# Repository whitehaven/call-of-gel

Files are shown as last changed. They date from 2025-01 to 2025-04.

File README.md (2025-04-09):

# call-of-gel

Trials to create ultrasound-compatible models for training purposes.

## Project Aims

It is important to note the primary goal is to create realistic models to generate high-fidelity practice repetitions linking Seldinger technique motor skills to live ultrasound navigation. This complex skill is the most challenging component of Internal Medicine procedures, especially when practiced at different scales and depths with different tools (arterial vs IJ lines). The specifics of individual procedures are relatively simple in comparison, e.g., all-in-one radial arterial line "darts" vs needle-and-wire kits.

- Create realistic ultrasound training materials approximating human tissue and vessels
  - target procedures are CVC and arterial line placement
  - this could be expanded to paracentesis, thoracentesis, and possibly lumbar puncture
- Acceptable candidate gel formulation would be:
  - nontoxic to create and require minimal materials beside  those found in medical contexts
  - nontoxic to handle
  - provide realistic ultrasonographic return
  - facilitate durable fluid-fillable lumens
    - these may be composed of surgical tubing or other components, but ideally they would be simple cast voids in the gel model which could be filled
- Ideal but non-critical characterstics:
  - Self-healing characteristic to lengthen longevity of created lumens
  - Recyclable/re-moldable by heating or other simple methods

### Future Directions

Requirements for Usable Models:

- [ ] multi-vessel gel mold

Investigational:

- [ ] consider alternative additives for echogenicity: sandblasting media (walnut shells, glass beads)
- [ ] consider agarose as gellant (admittedly no clear advantage other than smell)
- [ ] consider platicized PVC as alternative due to lack of odor and refrigeration requirement (complicated by creation requirement for vacuum chamber and lab-grade heating element at least)
- [ ] consider geometry of cast void which could be used as simulated vessel; otherwise obtain suitable vessel lumen material
- [ ] consider lumen material

## Trial 1 - **2025-01-16**

Mixture DOE with central augmentation. Assess `texture`, `echogenicity`, and `vessel_veracity`, all of which are required for an ultrasound model or "phantom." `Usability` characteristic was added post-hoc due to trouble with formation of tough cap in some cases that severely limited the utility of the sample without harming the gel's echogenicity in other areas.

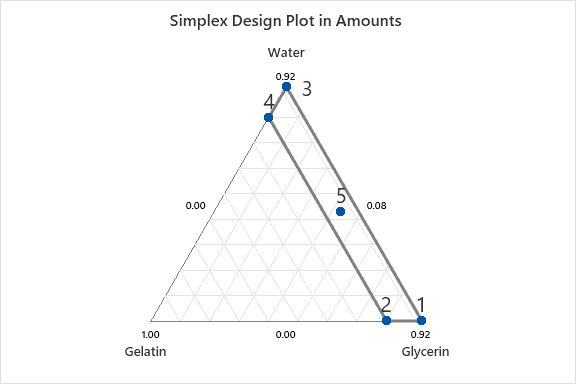
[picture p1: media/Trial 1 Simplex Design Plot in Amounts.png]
Trial 1 Simplex Design Plot


### Protocol

1. Base mixtures combined in 8oz party cup.
1. Gelatin mixed in to base mixture cold and slowly. Total mass for each was 150g.
1. Gelatin heated to 120-140F in double-boiler
1. Vessel mold (custom-thermoformed platicized PVC tubing suspended from baling wire in L-shape to create fillable simulated vessel) placed into each mixture.
1. When temperature achieved, cooled immediately to 40F for 8h.
1. Cast void lumens were filled with water by needle
1. Phillips Xtend unit was used to assess echogenicity

#### Deviations

1. Trial 1-5 took on a dense applesauce-like texture before insertion of vessel mold. The surface of the mixture had to be physically displaced by the mold. It reformed over the top spontaneously.
1. Trial 1-1 and 1-2 remained gooey after all other samples hardened. They are oily to touch and pull apart like thick applesauce. It is evident that glycerin content should not be greater than 50%.
1. Trial 1-4 was difficult to mix and generated extremely dense foam at the top during heating. It appeared to have retained air bubbles and was impenetrable to ultrasound due to scattering.
1. Trial 1-5 also generated dense foam, but the layer was about 2mm. It seemed to cause scattering as well, but much less so.

### Results

| StdOrder | RunOrder | PtType | Blocks | Water | Gelatin | Glycerin | test_g | water_g | gelatin_g | glycerin_g | resilience | echogenicity | usability | vessel_quality |
|----------|----------|--------|--------|-------|---------|----------|--------|---------|-----------|------------|------------|--------------|-----------|----------------|
| 1        | 1        | 1      | 1      | 0.00  | 0.08    | 0.92     | 150    | 0       | 12        | 138        | 1          | 1            | 0         | 1              |
| 2        | 2        | 1      | 1      | 0.00  | 0.20    | 0.80     | 150    | 0       | 30        | 120        | 1          | 1            | 1         | 1              |
| 3        | 3        | 1      | 1      | 0.92  | 0.08    | 0.00     | 150    | 138     | 12        | 0          | 2          | 1            | 3         | 2              |
| 4        | 4        | 1      | 1      | 0.80  | 0.20    | 0.00     | 150    | 120     | 30        | 0          | 3          | 1            | 1         | 2              |
| 5        | 5        | 0      | 1      | 0.43  | 0.14    | 0.43     | 150    | 65      | 21        | 65         | 3          | 2            | 2         | 2              |

(Where `test_g` is test mass in grams, and each ingredient specified as *_g is component mass.)

### Analysis

#### Mixture Plots

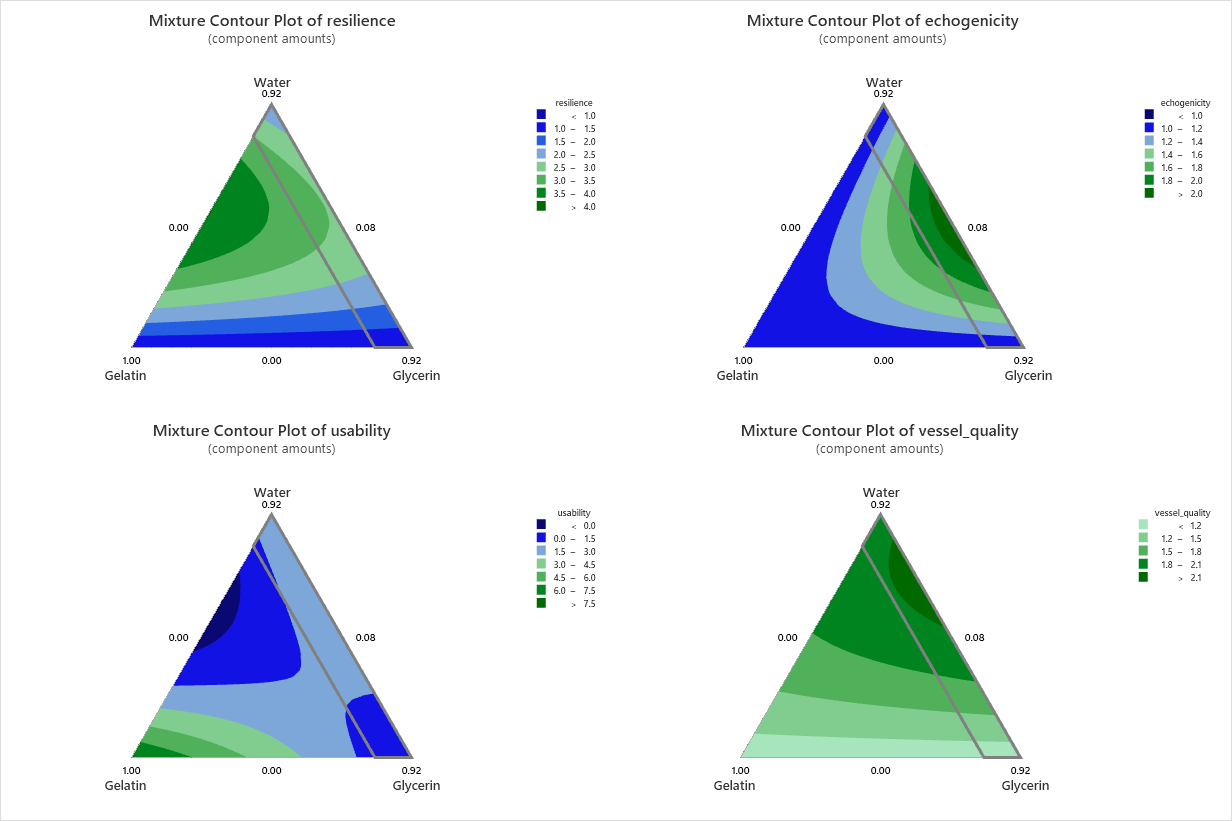
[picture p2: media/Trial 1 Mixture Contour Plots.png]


##### Conclusions

- Glycerin may help echogenicity but degrades resilience beyond 50%
- Echogenicity overall is pretty poor - additives needed

#### Response Optimization based on Trial 1

##### Parameters

|  | Goal         | Lower   | Target | Upper | Weight | Import |
|--------------|---------|--------|-------|--------|--------|---|
| resilience   | Maximum | 1      | 3     | 3      | 0.5*    | 1 |
| echogenicity | Maximum | 1      | 3     | 3      | 1      | 1 |
| usability    | Maximum | 0      | 3     | 3      | 0.5*    | 1 |
| vessel_quali | Maximum | 1      | 3     | 3      | 1      | 1 |

\* Weighting function modified to positive logarithmic shape to reflect that once adequate values are achieved, further pursuit of improvement is increasingly unimportant. Importance was not changed as the gel is unusable if these requirements are not met.

##### Global Solution

| Components |   |          |
|------------|---|----------|
| Water      | = | 0.557576 |
| Gelatin    | = | 0.08     |
| Glycerin   | = | 0.362424 |

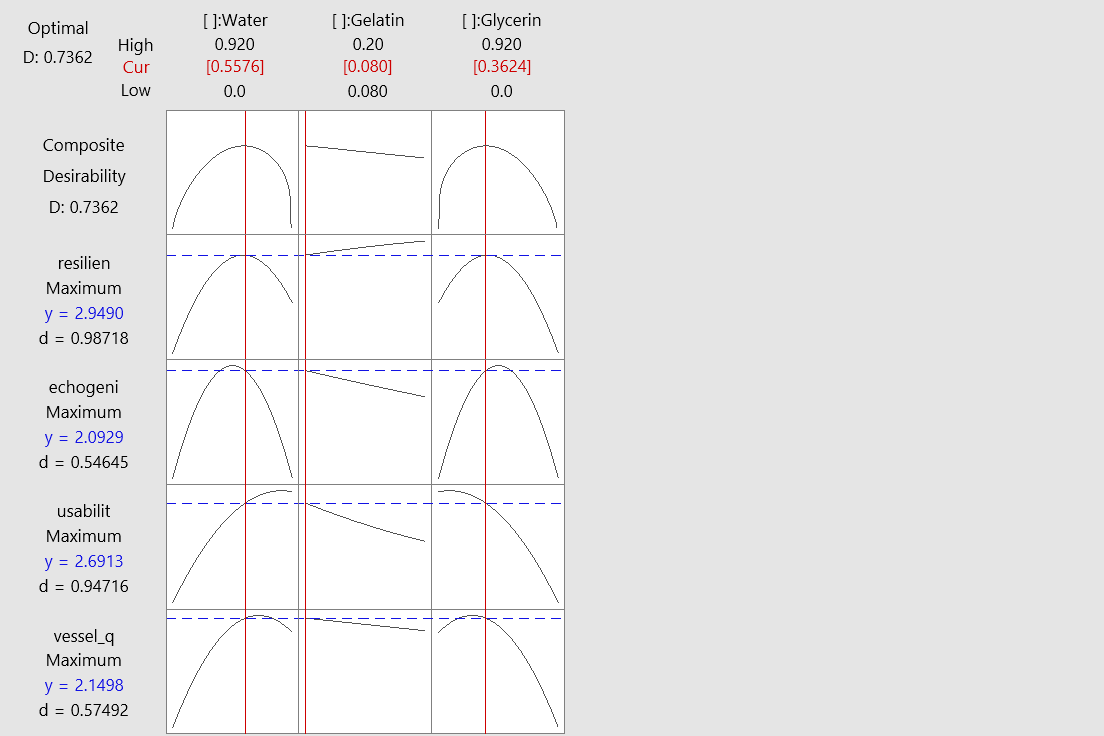
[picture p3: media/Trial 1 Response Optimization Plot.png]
Response Optimization Plot


*Addendum 2025-02-08:* More sophisticated analysis with JMP post-hoc with echogenicity electively removed due to low variance suggests the ideal mixture is as follows:

[JMP analysis report, captured at optimal solution](<media/trial 1-rereanalysis - Fit Least Squares.htm>).

Per JMP, global solution is instead:

| Components |   |          |
|------------|---|----------|
| Water      | = | 0.92 |
| Gelatin    | = | 0.08     |
| Glycerin   | = | 0.0 |

### Future Directions

- Glycerin should be no higher than 50%
- Glycerin possibly gives some self-healing quality
- 8% gelatin is almost perfectly durable, and 20% was challenging to use (low usability) - even though global solution shows 8%, suspect 10 or 12% may be optimal

## Trial 2 - **2025-01-21**

Proof of concept of psyllium husk (Metamucil) as echogenizer. Only 1 sample.

| Components |   |  Amount  |
|------------|---|----------|
| Water      | = |   91cc   |
| Gelatin    | = |    8g    |
| Metamucil  | = |    6g    |

### Protocol

1. Base mixtures combined in 8oz party cup.
1. Gelatin mixed in to base mixture cold and slowly. Total mass for each was 105g.
1. Gelatin heated to 120-140F in double-boiler
1. Vessel mold (5cm section platicized PVC tubing) placed directly into gel.
1. When temperature achieved, cooled immediately to 40F for 8h.
1. Cast void lumens were filled with water by needle
1. Phillips Xtend unit was used to assess echogenicity

#### Deviations

1. I intended to make 100cc total gel, however due to low scale precision, too much water was added. The net mass fraction of gelatin was under 8% which is generally regarded the lowest possible concentration.

### Results

- Psyllium husk massively improved echogenicity.
- Immersing the PVC tubing section feasible rather than more complex wire mold hanger. The tubing must exit the gel when solidified though, however. It naturally floated 1mm or so above the surface so this was not a problem. It was removed with hemostat with rotational traction.

### Analysis

- Psyllium is effective, but it is not clear how this relates to needle tract formation.
- Needle tract formation problematic
  - possibly related to low glycerin concentration leading to excess deformation.
  - possible related to psyllium effect (hopefully not)
- Query anti-tract effect of glycerin which may facilitate some natural self-healing.

### Future Directions

- Larger trial needed to incorporate psyllium ranges and the useful ranges of glycerin (<=50%) (possible self-healing property from initial trial)

## Trial 3 - **2025-02-08**

This will be 20-run larger mixture optimization experiment with full Scheffe cubic targets if possible, but prioritizing 1st order terms - *a priori* I don't suspect massive interactions.

Broadened targets to base echogenicity, modulus, needle friction, and remnant needle tracks. All but remnant needle tracks are targeted at optimal, 0, lying between -3 and +3. Remnant needle tracks are to be minimized from 0 to +3.

The 0/+1/+2/+3 system is a widely-used ordinal severity measure in medicine. It can be taken thus in most contexts:

| ordinal scale | qualitative impression | proportion of the worst known case of this finding |
| --- | --- | --- |
| 0 | absent | 0-25%* |
|+1 | mild | 26-50%*|
|+2 | moderate | 51-75%*|
|+3 | severe | 76-100%* |

I have chosen to use this scale due to familiarity. The +4/extreme level will not be used.

Switched to JMP - better DOE than Minitab - more sophisticated planning and analysis functions. See comparison: [Minitab file](<trial 3 plan.mpx>) vs [JMP 17 file](<trial 3 plan.jmp>).

Tabulated form [here](<trial 3 plan.xlsx>).

### Post-experiment tasks

Will attempt to "heal" tracks if present in most or all aliquots. Reportedly this can be done with application of heat - low temp on heat gun or hair dryer.

My own ideas are also to try brief MAP torch application if heat gun struggles to penetrate, or to heat needle with heat gun and briefly reinsert along track, or finally to inject tract with some degree of heated water (perhaps microwaved).

## Trial 4 - **2025-02-17**

I became curious about the relative benefits of agar compared to gelatin as described in **Earle, et al.** Most prominently, the risk of mold/rot is much decreased. Earle, et al. describe a test over 2 weeks unrefrigerated with only shrinkage.

I did a simple test of their recommended composition of 5% agar with flour and psyllium as echogenizers, and I was suitably impressed.

Notably I tried to double-boil plastic cups with the mixtures chosen, however I am not sure I reached boiling in all three samples, as I reached plastic deformation of the cups before I was able to confirm temperature. All 3 were 100cc aliquots.

| mixture | echogenicity | modulus | needle friction | needle tract visibilty |
| --- | --- | --- | --- | --- |
| 5% agar | 0 (poor) | 0 (near-perfect) | 2- (moderately too easy) | 0 (no detectable tracts) |
| 5% agar + 2.5% bleached flour | 2+ (good) | 1- (somewhat too soft) | 2- (moderately too easy) | 0 |
| 5% agar + 2.5% psyllium husk | 1+ (fair) | 2- (barely usable) | 3- (much too easy) | 0 |

**Earle, et al.** also suggest lining the top of the phantom with a single layer of disposable glove. This can easily be created by removing the fingers and splitting the glove along the hypothenar eminence. This would add to the realism of penetrating the skin followed by soft tissue. The original paper recommends adding this to the top before final cooling, but with some traction I made it work after the fact. There was no appreciable change in image characteristics.

### Representative Images

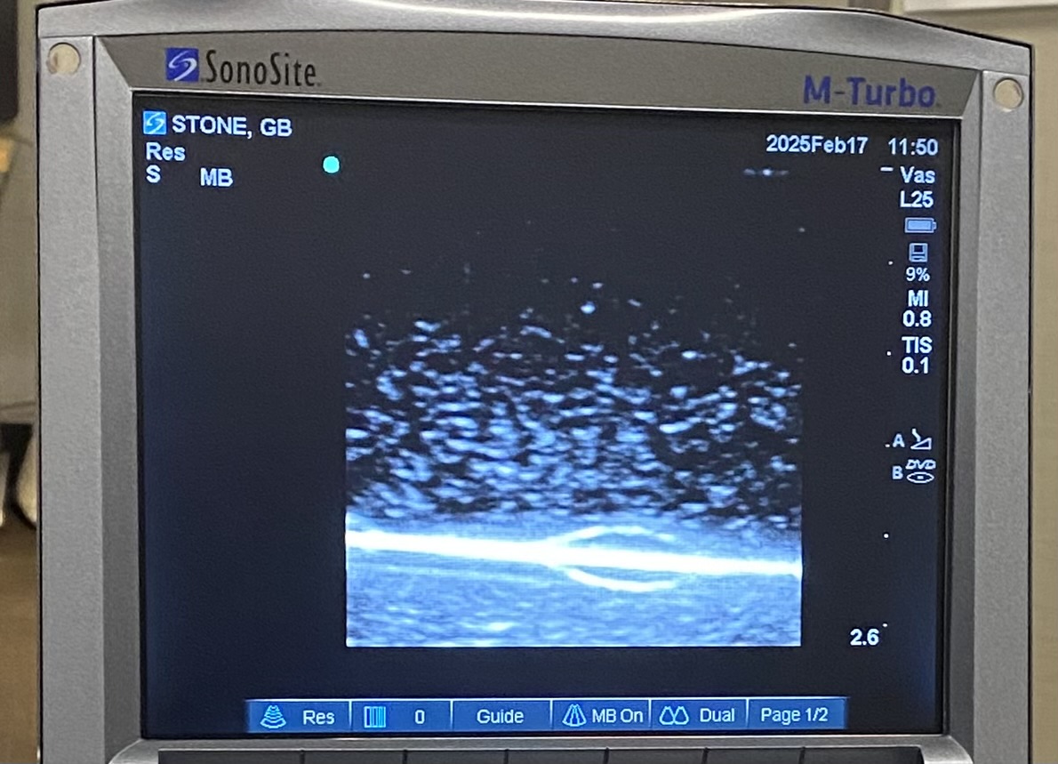
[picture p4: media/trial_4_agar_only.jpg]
5% agar
>
> 5% agar

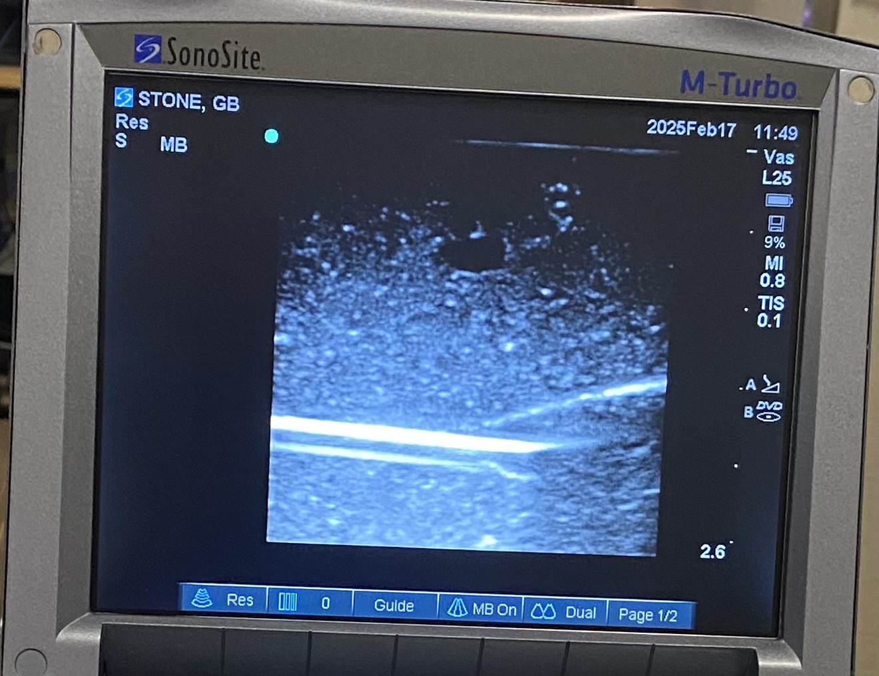
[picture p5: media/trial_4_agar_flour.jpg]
5% agar + 2.5% bleached flour
>
>5% agar + 2.5% bleached flour

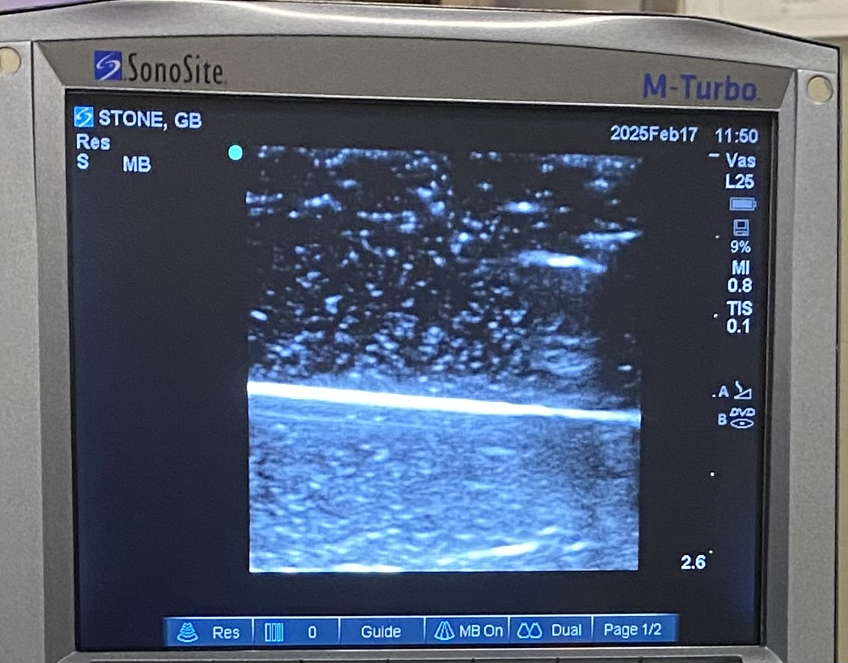
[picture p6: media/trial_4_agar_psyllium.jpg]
5% agar + 2.5% psyllium husk
>
>5% agar + 2.5% psyllium husk

They did not do well over 5 day longevity test.

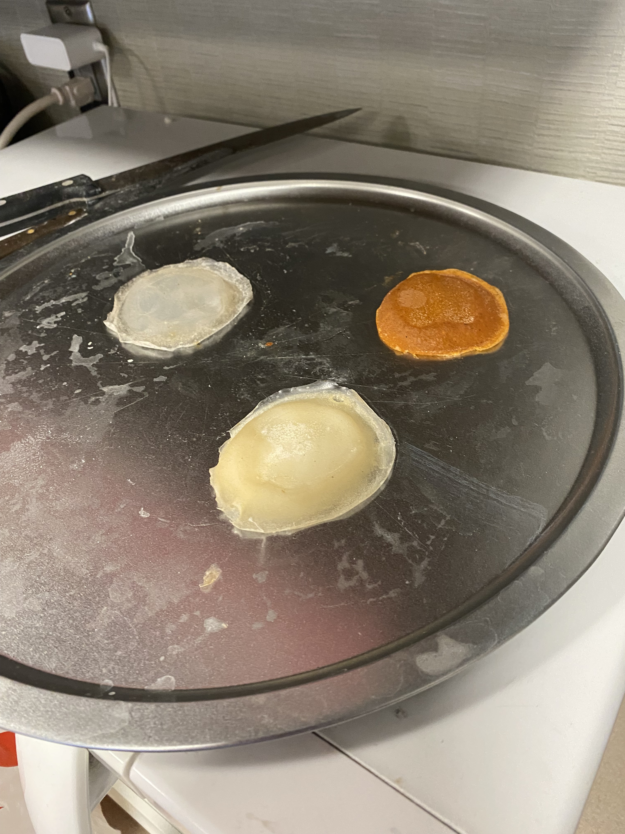
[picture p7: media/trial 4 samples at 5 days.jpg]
trial 4 samples at 5 days


### Conclusion

I am reorienting my efforts to agar - it does not require refrigeration, achieves a highly tissue-like consistency, and can reportedly be repaired easily in microwave. As it is carbohydrate-based, it is not as sensitive to heat as gelatin.

## Trial 5 - **2025-02-21**

Tried **Earle, et al.** suggestion of 5% agar and 1 tsp flour in 750cc (0.65%).

Flour difficult to mix fully, clumped at bottom. Echogenicity was still quite good, though compacted toward the mold bottom. This was corrected easily with the half-image gain adjustment.

Silicone tubing was trialed as candidate material - tubing much too resilient to needle puncture. Also tried removing the tubing and replacing the void with water, which eliminated entry force to the lumen. Have yet to trial natural rubber latex tubing which I expect will be more readily pierced.

The tubing was passed into the containter mold without piercing the walls, taking on a U-shape. The tubing couldn't be pressed down, as it would end up too shallow to the bottom of the casting, leading to leaking. The  usable tracts are quite short. The authors of **Earle, et al.** suggest a two-layer pouring process, but this creates a strong layer artifact. It would, however, enable greater force to be used to bend the tubing. Ultimately I believe passing the tubing directly through the mold wall with reversible water tight seals (PU hot glue) is the best option to maximize usable vessel area, but could consider multi-layer. There may also be a role for spacers and positioning aids inside the mold body, but again this sacrifices usable area.

Data added to `trial 4 with initial data.jmp` for analysis. Still not enough variance for any patterns to emerge when analyzed.

### Representative Images

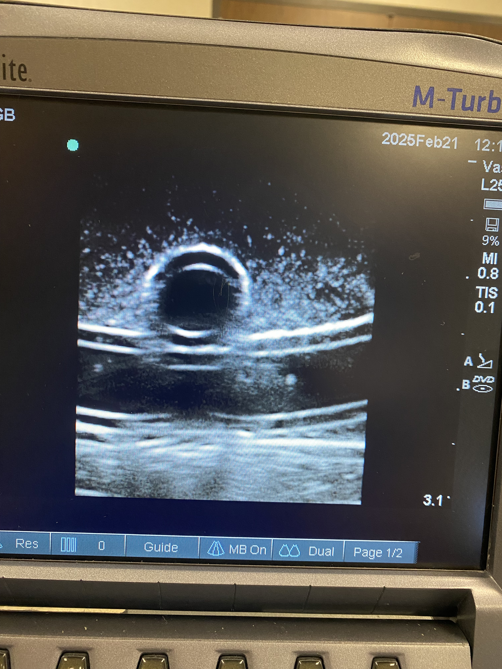
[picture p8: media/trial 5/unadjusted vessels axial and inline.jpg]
>
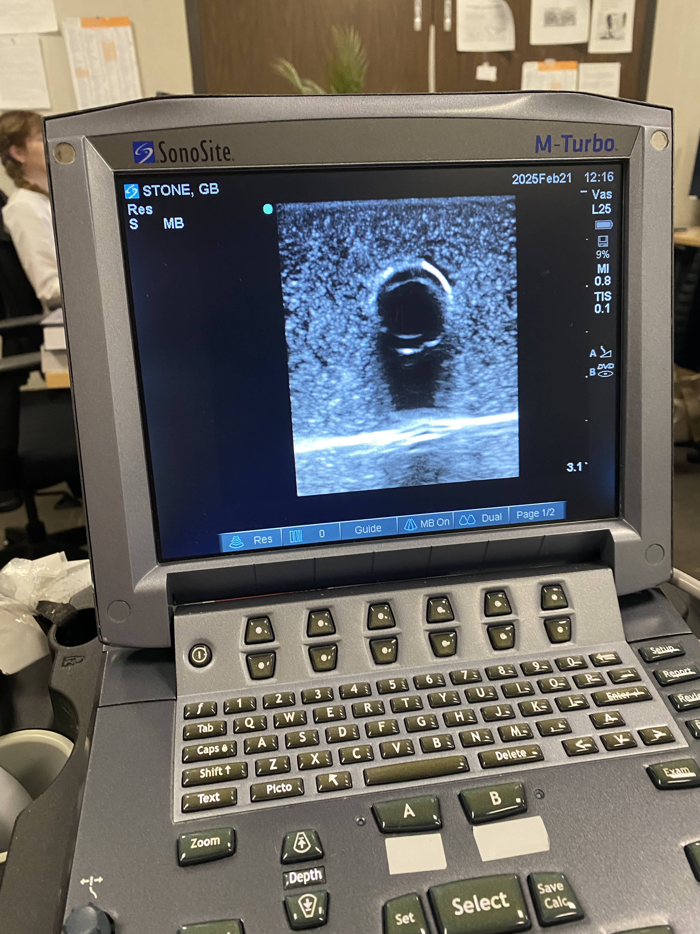
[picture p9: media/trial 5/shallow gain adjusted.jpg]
>
>pre- and post-gain adjusted images 

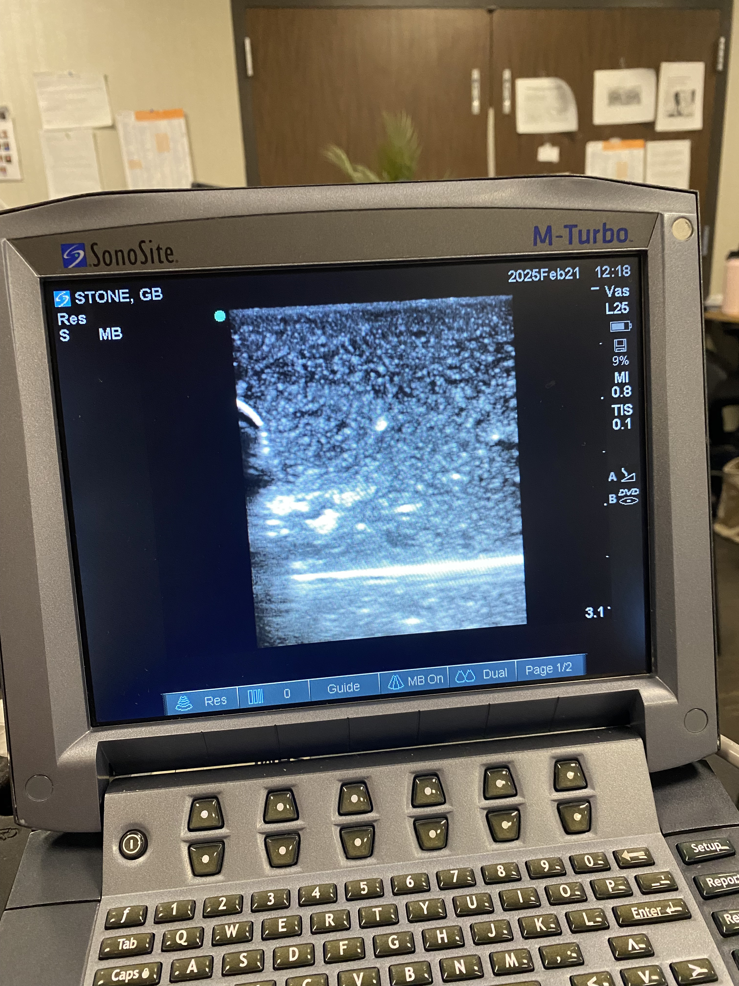
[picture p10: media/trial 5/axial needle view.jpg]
>
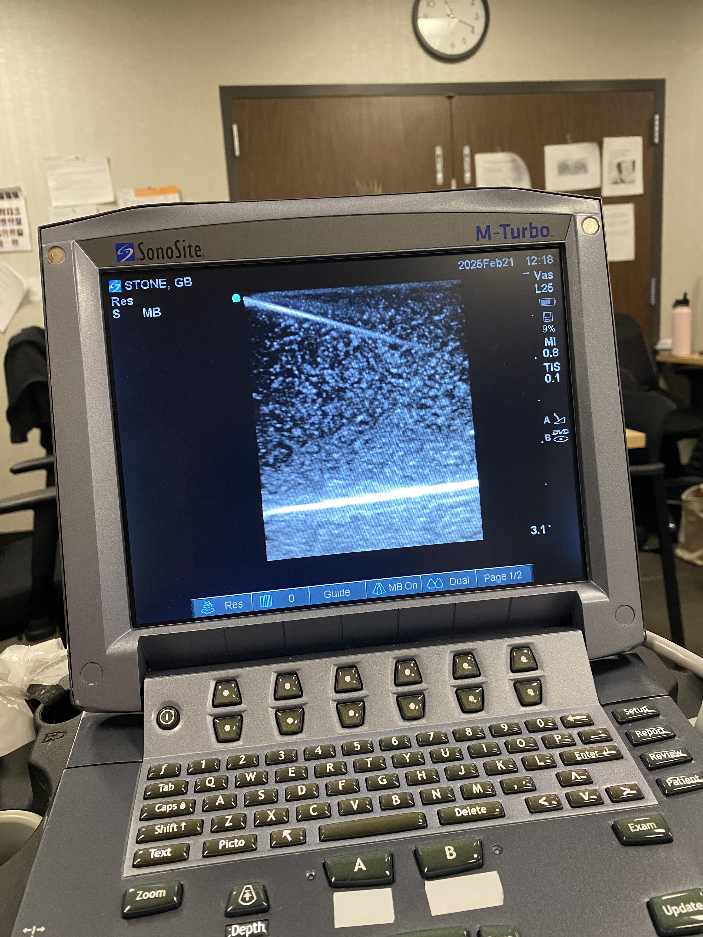
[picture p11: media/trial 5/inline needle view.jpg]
>
>needle views

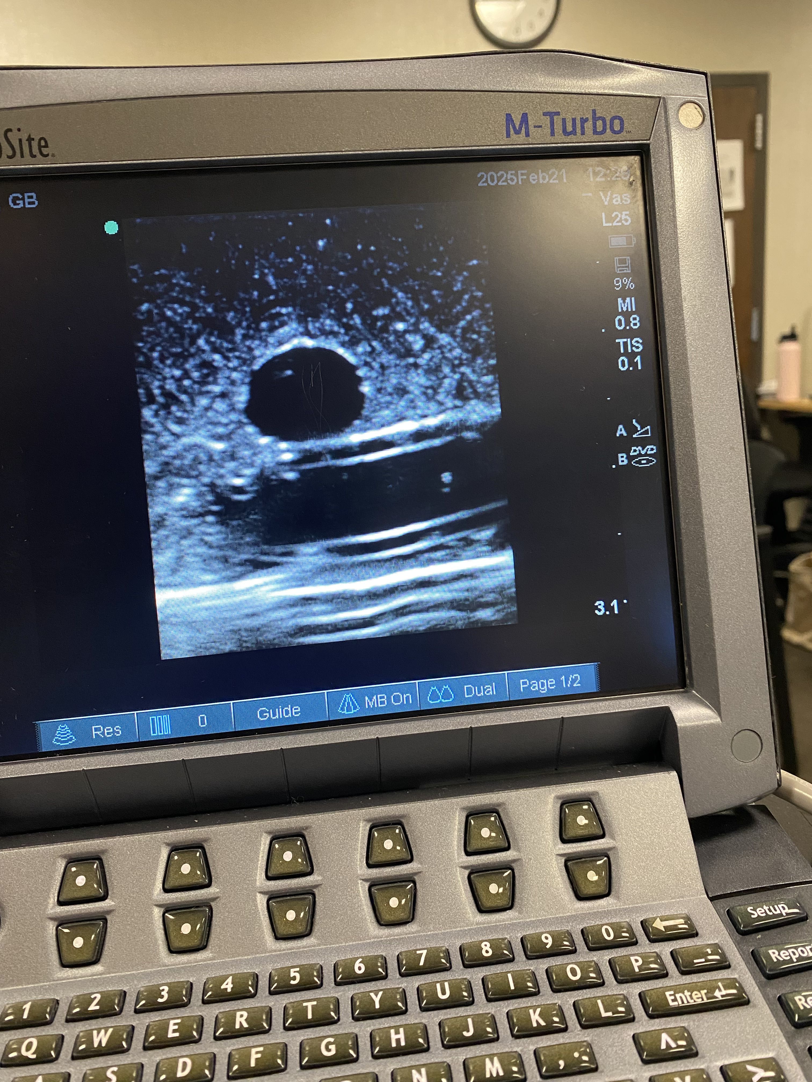
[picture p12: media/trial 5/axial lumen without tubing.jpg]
>
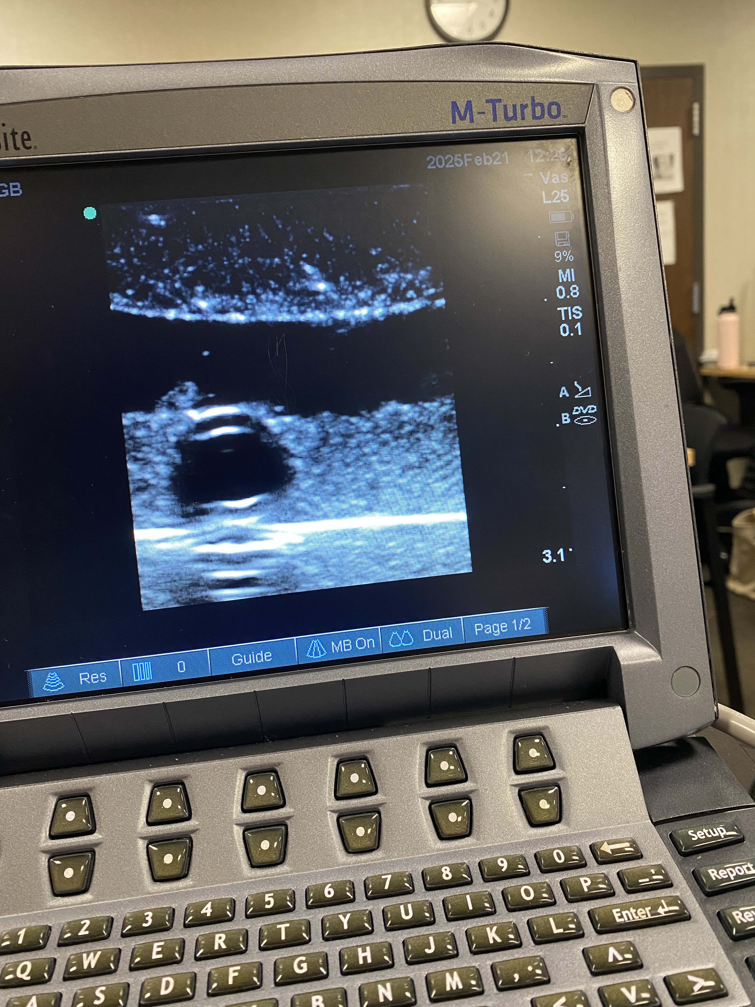
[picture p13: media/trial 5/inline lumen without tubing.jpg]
>
>lumen without tubing (the more shallow void)

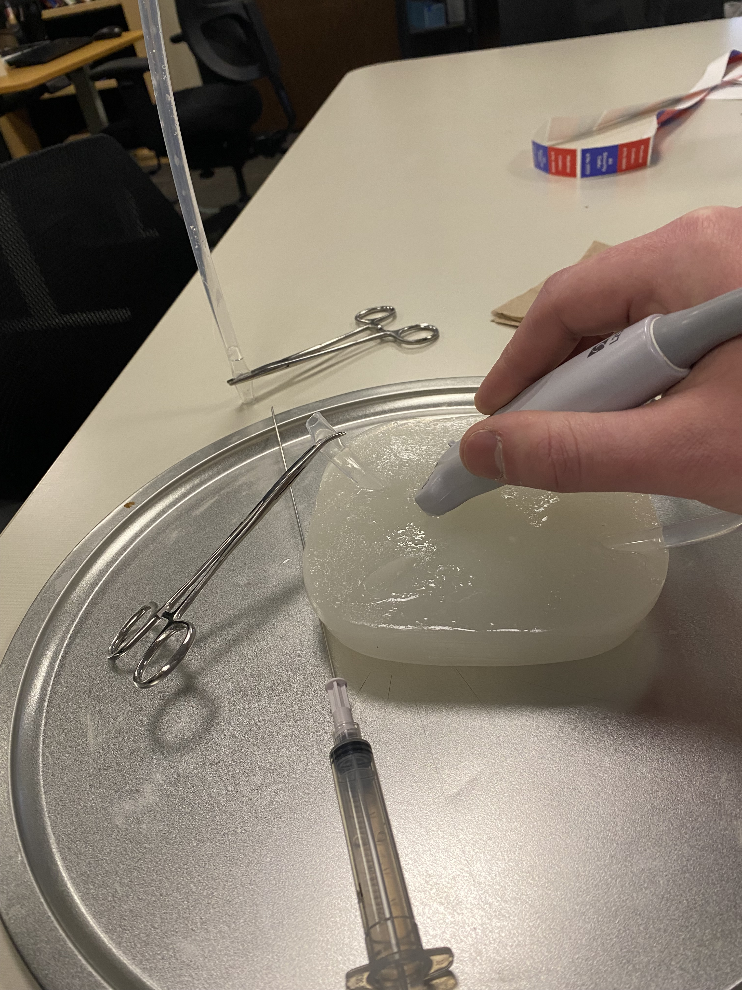
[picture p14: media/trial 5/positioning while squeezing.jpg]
>
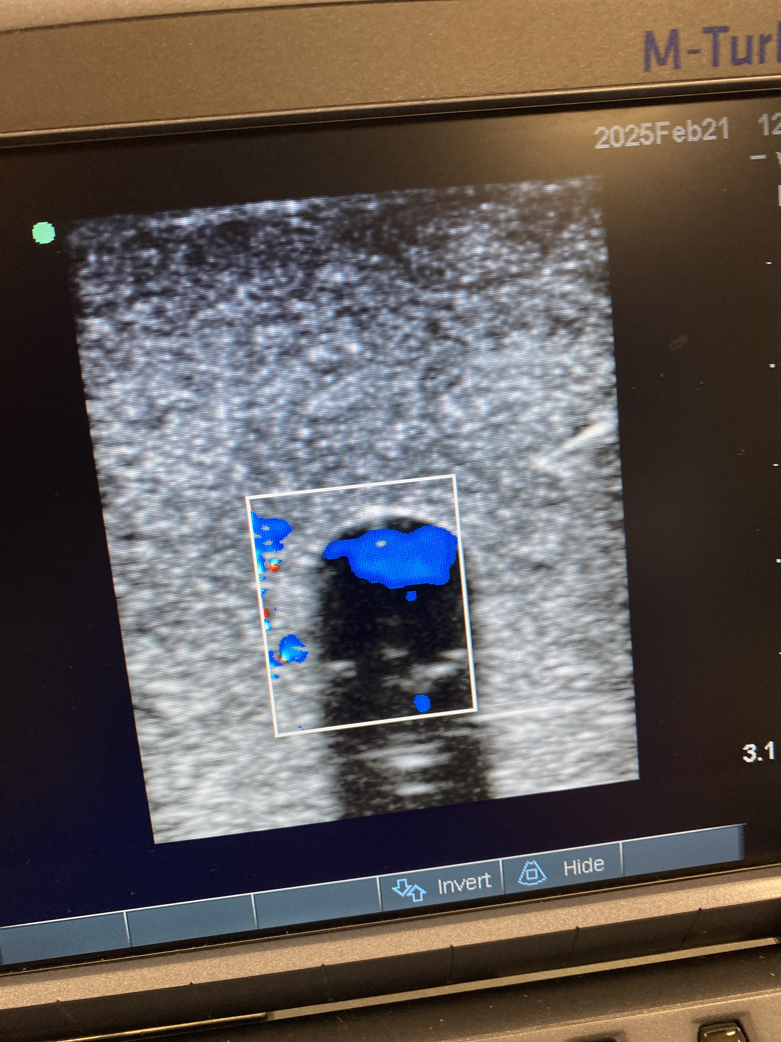
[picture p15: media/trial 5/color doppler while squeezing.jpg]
>
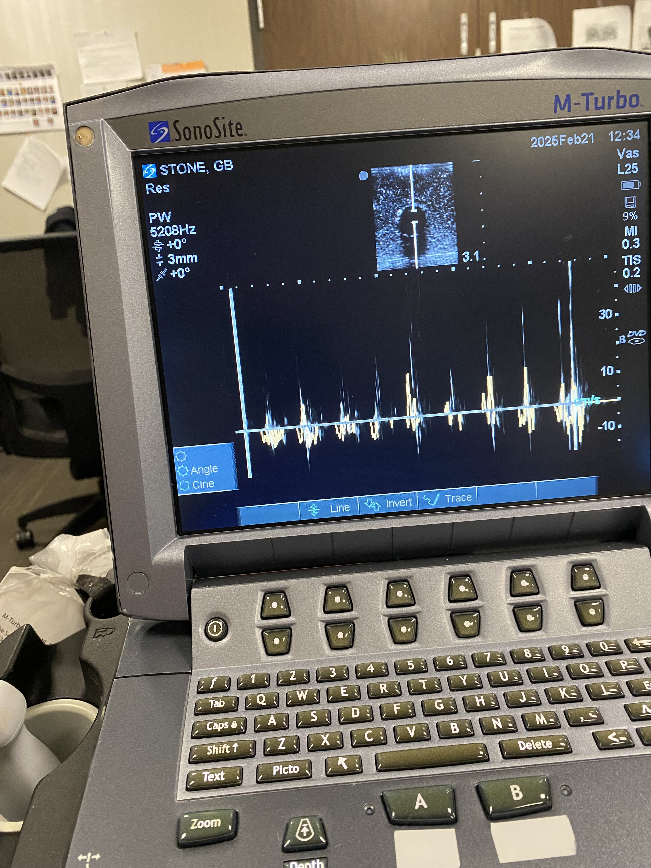
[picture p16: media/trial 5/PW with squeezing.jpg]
>
>power and color doppler while rhythmically squeezing sealed tubing section

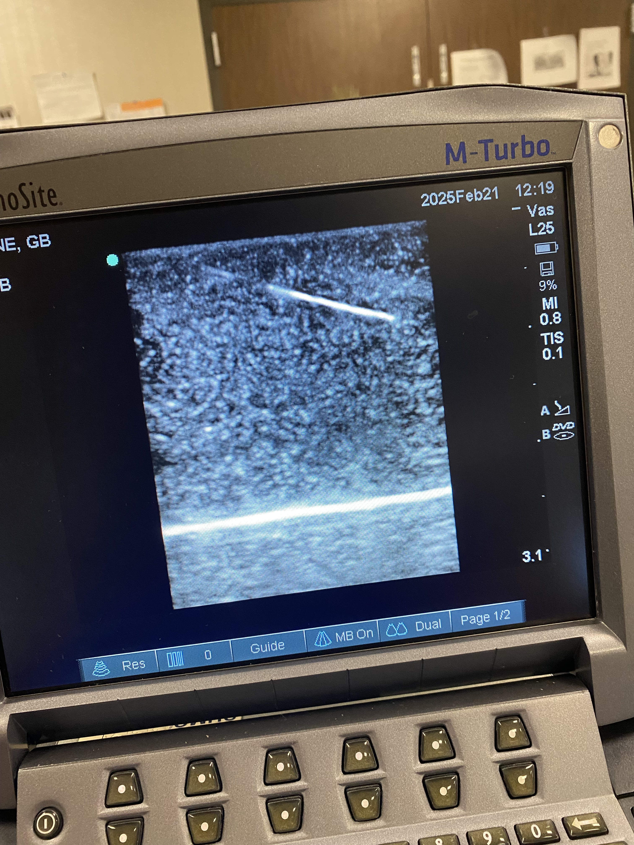
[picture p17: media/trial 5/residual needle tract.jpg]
>
>residual needle tract
---

## Trial 6 - **2025-03-28** *(informal)*

Made 2 gels of 7.5% agar, 0.5% all-purpose flour, 1.5 and 1.25L samples. A few mL 70% isoproypl alcohol was used as a degassing agent as well.

Ran 12mm OD/8mm ID  natural latex tubing to represent IJ, and 4/3 tubing for radial arteries. They looked right, if a little too regular.

Used for simulation lab training with new residents who had done 0-2 central lines in their careers.

Very good imaging characteristics, but didn't perform detailed analysis.

Excellent needle visualization, tenting of vessel.

Unfortunately, they rotted at 10 days despite being bagged, likely related to the wet flour content.

Optimal solution probably is flattened nitrile glove skin on agar at 7.5% with irregular surface (anterior triagle of the neck) to train probe placement. I expect a FDM solution would be suitable.

An echogenizer that doesn't rot is also of interest.

## Bibliography

> Earle M, Portu GD, DeVos E. Agar ultrasound phantoms for low-cost training without refrigeration. Afr J Emerg Med. 2016;6(1):18-23. doi:10.1016/j.afjem.2015.09.003

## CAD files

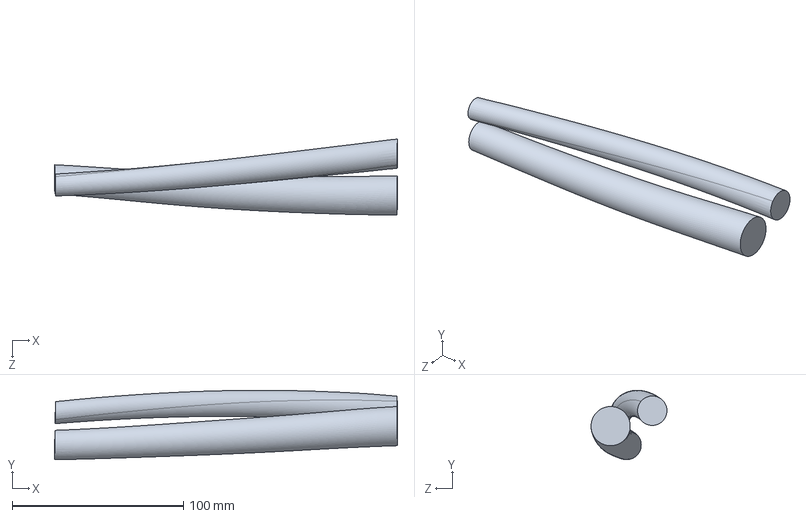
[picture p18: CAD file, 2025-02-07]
carotid-IJ mold.SLDPRT
200.3 x 40.5 x 44.4 mm

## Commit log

2025-02-07 carotid-IJ mold with draft angle to be removable to leave void
    [carotid-IJ mold.SLDPRT]
2025-02-09 replan trial 3 with JMP 17, finalize factors, add needle friction
    [trial 3 plan.xlsx]
2025-02-17 add ultrasound images of new agar samples
